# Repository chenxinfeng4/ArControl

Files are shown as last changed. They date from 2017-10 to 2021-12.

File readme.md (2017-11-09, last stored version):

# ArControl Guidence
---
+ Author: Chenxinfeng
+ Email  : chenxinfeng@ibp.hust.edu.cn
+ Copyright (C) 2017, Huazhong University of Science and Technology.  GNU LGPL v2.1.
+ Source-code download: https://github.com/chenxinfeng4/ArControl
+ Binary-release download: https://github.com/chenxinfeng4/ArControl/releases
+ PCB drafts download:  https://github.com/chenxinfeng4/ArControl/releases

## Introduction

---
### What's the ArControl

The goal of ArControl is to establish an Arduino-based (UNO only) behavioral platform, which control devices to deliver stimulation and monitor behavioral response. It's a powerful solution for behavioral researches.

The basic features of this platform include: 

+ Comprehensive – it combines software and hardware, behavioral task design and experimental data collection; 

+ Inexpensive – neither dedicated nor expensive hardware is essential;

+ General purpose – it’s applicable to multiple behavior tasks; 

+ Easy to use – behavior task can be decomposed by the straightforward State Notation concept, and designed via a friendly GUI without need to master script language.

+ Real-time performance – it has high temporal resolution and free from the load of computer.

,



> **Diagram and hardware of the ArControl’s electroniccircuit**. (**a**) Overview of the electronic circuit. Arduino is the core controller detects animal response, sends simulations via digital pin, and logs data to the host computer. ArControl supports 6 input and 8 output digital channels. (**b**) The hardware of ArControl: Arduino Uno R3, the driver circuit for voltage conversion. (**c**) The driver hub provides slots for terminal devices. Sensors can work at 5V, and stimulators can alternatively work at 5/12V.

### ArControl uses State Notation to design tasks

Inspired by Graphic State Notation, we succeeded in grafting State Notation Pattern into ArControl platform (**Figure 2a, b**). The schedule is constructed at hierarchical levels: Session (top), Component (middle), and State (lowest). The State is the basic structure using State Notion design pattern. The Component and the Session are the primary and the secondary collection of States (**Figure 2b**). Generally, the terms of Session, schedule, and behavior task are equal concepts indeed. Utilizing the State Notion Pattern, a schedule is dissembled as a serials of States. Each State specifies a stimulus configuration in subject’s environment and a set of time and/or response requirements that cause state transition (**Figure 2a**). There is one and only one State to be active at any moment. Session will sequentially move from current State to next State, until reaching the terminal. 



>**Figure 2 Diagram of State Notation Pattern utilized by ArControl. **(**a**) The State has a *do-function*
>to deliver stimulus, and *when-functions *to master transitions cross States. (**b**) The Component and Session structures are the primary and secondary collection of States.

### ArControl has tow parts of GUI

The ArControl software suite consists of two individual parts -- the Designer (**Figure 3a**) and the Recorder (**Figure S1a**) -- for the purpose of designing and running a Session respectively. The ArControl Designer is core program, where users apply State Notation concept to achieve the Session construction.

The ArControl Recorder is the other part of ArControl software suite. The basic functions of it contain clicking to start/stop running ready Session, collecting the data flow and displaying as table and chart contents (**Figure S1a**). Besides, there is a straightforward utility tool plugged in —Firmata— intent to debug the input and output devices.

The two parts can run individually. In the source file, they are named as **"arcDersigner.exe"** and **"arcRecorder.exe"**

ArControl GUI logo



> **Figure 3.** Apply ArControl-Designer to design Session. (**a**) The main window of ArControl-Designer.
> It supports two *do-function *and four* when-function* types for each State. (**b, c**) Typical pop-up windows to configure a *do-function *(**b**) and a *when-function *(**c**). (**e**) The layout defines and
> initializes the global variables, which can be share among States.



> **Supplementary Figure 1. The data collection from ArControl. **(**a**) The main window of ArControl-Recorder. (**b**) The serial monitor window of ArControl-Recorder. Numbers after colon represent the beginning and duration time in milliseconds. (**c**) A matched segment extracted from the data file.

## Install ArControl

---
### Download and install Arduino IDE

ArControl relays on Arduino-IDE. You should download the IDE from offical [site](https://www.arduino.cc/en/Main/Software).

- The ArControl was verified on [Arduino IDE 1.6.11](https://www.arduino.cc/en/Main/OldSoftwareReleases#previous) . In theory, the latest versions are also eligible, except 1.6.12.

- You are recommended to download the "Windows Installer" version.

  Arduino logo

### Download and install ArControl

As for general purpose, the [**binary-release**](https://github.com/chenxinfeng4/ArControl/releases) version are recommended. ArControl is only verified on **Microsoft Windows PC**. You can recompile the [**source-code**](https://github.com/chenxinfeng4/ArControl) to make adaptations.

+ If you want to use binary-release directly, just download and unzip it.

+ Onlyif you want to compile source-code, you should download and install [Qt5.7](https://info.qt.io/download-qt-for-application-development). 
+ ArControl will automatically look for any available "Arduino IDE". Make sure that you have installed the "Arduino IDE".

Qt logo

##  Your first task  -- "Light3"
---

### Compose your first task  -- "Light3"

It's nature that different choices lead to different results. It's our first task to follow this schedule (below).  Even a proficient programmer may takes half an hour to implement such schedule, using Arduino C++ langue. However, ArControl makes things easier even for beginners.

shedule

> The sequence of events in **Light3 task**. You will get Yellow Ligth (4sec)  Green Ligth (3 sec) or Red Ligth (2 sec), depending on the your choice of Left, Right or Wait.

The schedule was decomposed with ArControl Designer as figure below. This demo has been embeded in release version, and it can alse be found in `ArControl Designer> File > Open in > Light3`.

Light3

>  The schedule was decomposed with ArControl Designer. Besides, an extra restraint ("max loop = 100 -> Exit Session") were added.

Priority ranks

> Priority ranks (sequences) of `doXXX` and `whenXXX`. Items in `whenPin` are in equal priorities.

Light3 run

> Run a "Light3" task. Data was viewed as log in "Data Stream" pannel, as table in middle pannel, as chart in right pannel, and was collected to data file under "Datafile Folder".

### Insights into the task  -- "Light3"

The `ArControl Designer` saved the previous `Light3` layout as *Light3.aconf*, and automaticaly generated executable *Light3.ino*. 



Light3.ino

The `ArControl Recorder` automatically saved the log to data file. You can use my Matlab function `BF_arc2mat.m` to convert the file from TXT to MAT.





## Other ready demo tasks -- "Go_NoGo" / "2AFPC" task
---
Two common behavior tasks, a Go/No-Go task (Gomez et al., 2007; Dolzani et al., 2013) and a two-choice procedure task (Tai et al., 2012; Stephenson-Jones et al., 2016) which have been widely applied to assess discrimination and memory. Here we implement their logics by ArControl.

### About this two task

The schedules were illustrated as figures below. This demos have been embeded in release version, and can be found in `ArControl Designer> File > Open in > Go_NoGo` and `ArControl Designer> File > Open in > twoAFPC` . 

Go_NoGo schedule

> In the **Go/NoGo task**, mice were body restricted via a head bar and body tube (Guo et al., 2014) and were required to discriminate a go cue (tone) and a no-go cue (light). They would consequently get a reward (water-drop) or a punishment (air-puff) once they respond (lick) to the go cue (tone) or no-go cue (light) during a response window, respectively.

2AFPC task

> In the **2AFPC task**, animals were required to initiate a trial by licking the central port, and sequentially move to a left or a right port to obtain a reward. Only one port was rewarded by 75% at a time. In 25% of trials, neither port was rewarded. If no reward was delivered, animals would be punished with an extra time out. Rewarded port was periodically switched across time.

## Resolution for Common Problems of ArControl Software
---
###  **Recorder Error**: Messages are Messy Coded when uploading a task.
Arduino IDE should be configure as "English" language. Open `Arduino IDE > File > Perferences > Editor language`, choose `English (English)`.

### **Recorder** Error: Crash when uploading a task.
Make sure that you have installed Arduino IDE, the Arduino IDE path is valid. You should renew the path of  Arduino IDE. Open `ArControl Designer > File > Profile > Arduino IDE path`, choose the valid  `arduino_debuger.exe` (for Windows) under the root of  Arduino IDE path.

### Recorder / Designer Error:  Crash immediately when opening

It may caused by wrong configuration of `ArControl`. You should reset the software. Delete `default.bconf` (if exsits), `task\defalut\` (if exsits) and `profile.xml` (if exsits).

### Recorder Error:  A "Time Out" Error when uploading a task.

It's common for a fresh task.  Try to repeat, or try to use `ArControl IDE` to upload the task.

### Recorder Error: Cannot connect to Arduino board

It's common when the Arduino board is currently occupied by other program (etc., `Arduino IDE > Serial Monitor`). Reject the Arduino board from this program, or reconnect via the USB port.

### Recorder Error: "fatal error: xxxxx/ArControl_AllinOne.h: No such file or directory"  when uploading a task

Open  *mytask*.ino, find the line `#include "xxxxxx/ArControl_AllinOne.h"`. The path may be invalid. Renew this path mannually, or resave the *mytask* via `ArControl Designer`.

### How to: Choose language of ArControl
ArControl now merely supports `简体中文` and `English` languages.  Swithing language by -- `ArControl Designer > File > Profile > Language`, `ArControl设计师 > 文件 > 选项 > 语言`.

### How to:  Regard the "whenPin" INx as HIGH or LOW voltage.

Typical sensors reflect resting-status at LOW, and activating-status at HIGH voltage. However, some sensors are opposite coded. Open `Arcontrol Designer > File > Profile > Input signal as`, choose the proper option and it works for all **INx** .

### How to: Start a task immediately or by Hardware-Trigger

A task is commonly triggered by `ArControl Recorder > START` button. However, the task can triggered from other style.  Open `ArControl Designer > File > Profile > "Start" Model`. There are `immediately`, `Trigger by Hardware (pin_11_HIGH)`, `Trigger by: Software (serial communicate)`, `Trigger by: Software or Hardware`.

### How to: Timer-Stop a task

A task is stopped typically from 1. `ArControl Recorder > STOP` button; 2. The task has finished its' schedule (terminates at`C0` or `CxS0`). In addition, you can set a **Timer-Stop** from the `ArControl Recorder > Timer window` .

Timer-Stop

### How to: Use Arduino IDE to run a task

You can use the `ArControl Designer`, as well as `Arduino IDE` to run a task. Open the `Arduino IDE > Serial Monitor`, choose the `250,000 baund` and send the character `b`.

letter b

## Skills and Warns
---

### Warn: Parameters value "`0`"-- special purposing 

Avoid to use `0` as the value of parameter in `ArControl Designer`.

parameters 0

### Skills: Parameters value support Variables 

Global Variables are defined in `Edit > Var Assignment`, dynamicly refreshed in `doVar` or `whenVar`, sharable among States, practicable for parameters value.



### Warn: 20 States are the maximum size of a task

Limited with the 2Kb SRAM of Arduino UNO, 20 States are the maximum size of a Session. 

### Warn: 200 Hz is the maximum frequence of [INx]

ArControl could record 200Hz TTL signal from all 6 input channels simultaneously, and 700Hz when focusing on a single channel, with ±1ms (95% confidence, round effect) accuracy around the truth.

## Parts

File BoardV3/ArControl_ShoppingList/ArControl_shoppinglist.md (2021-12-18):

# ArControl PCB 采购清单
## Arduino Nano (Type-c)
[购买链接](https://item.taobao.com/item.htm?spm=a230r.1.14.12.68d3196cPjnAZf&id=646565255962&ns=1&abbucket=10#detail)

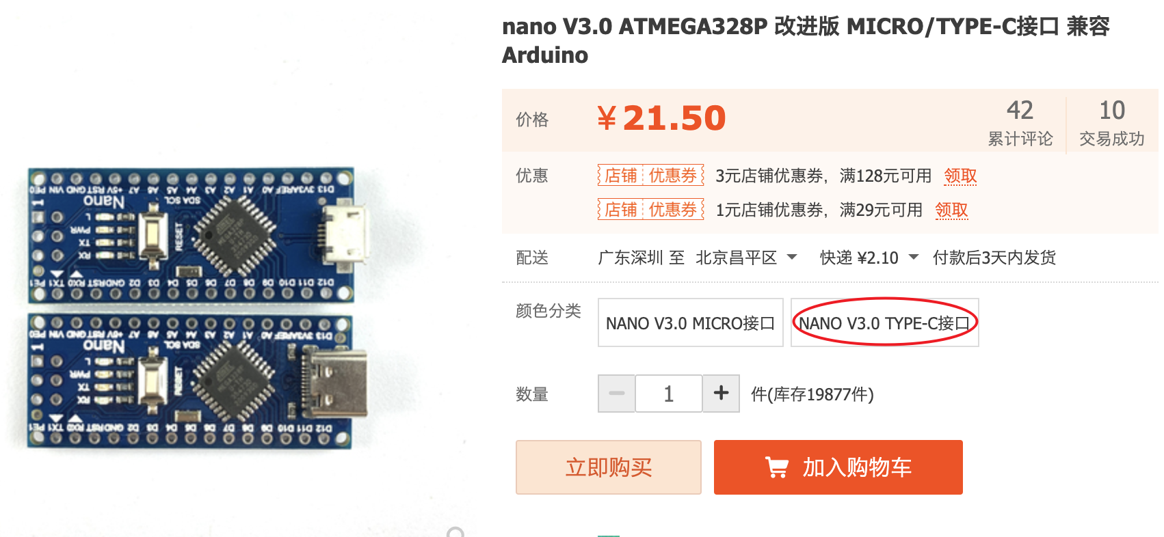
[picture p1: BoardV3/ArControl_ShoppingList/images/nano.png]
demo1


## PCB板打印

[加工链接](http://www.sz-jlc.com/home/factory.html)
+ BoardV3/PCB/Optogentics_Controller.PcbDoc

说明: 收到的是“裸板”，元器件需要自己焊接。

## 外壳3D打印
+ BoardV3/CaseModel/Case1.stl
+ BoardV3/CaseModel/Case2.stl

找淘宝打印

## Type-C数据线
[购买链接](https://detail.tmall.com/item.htm?spm=a220o.1000855.1998025129.2.60eb473cbVLz9X&id=529091830072&scm=1007.12144.95220.23864_0_0&pvid=ef18f5ed-d7ec-41bb-b568-07af17dbfef6&utparam=%7B%22x_hestia_source%22:%2223864%22,%22x_object_type%22:%22item%22,%22x_hestia_subsource%22:%22default%22,%22x_mt%22:0,%22x_src%22:%2223864%22,%22x_pos%22:2,%22wh_pid%22:-1,%22x_pvid%22:%22ef18f5ed-d7ec-41bb-b568-07af17dbfef6%22,%22scm%22:%221007.12144.95220.23864_0_0%22,%22x_object_id%22:529091830072%7D&sku_properties=148242406:21516)

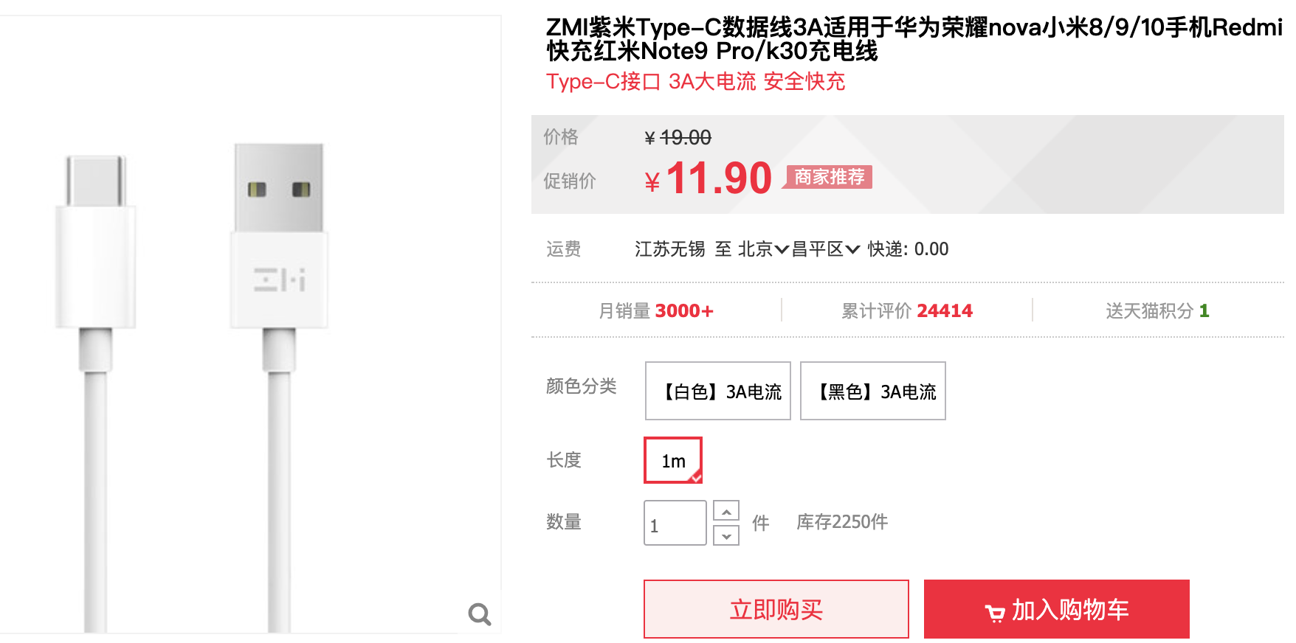
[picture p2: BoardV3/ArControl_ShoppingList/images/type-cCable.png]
demo2


## 三芯 3.5mm音频延长线，转接线
[购买链接](https://item.jd.com/7663022.html)

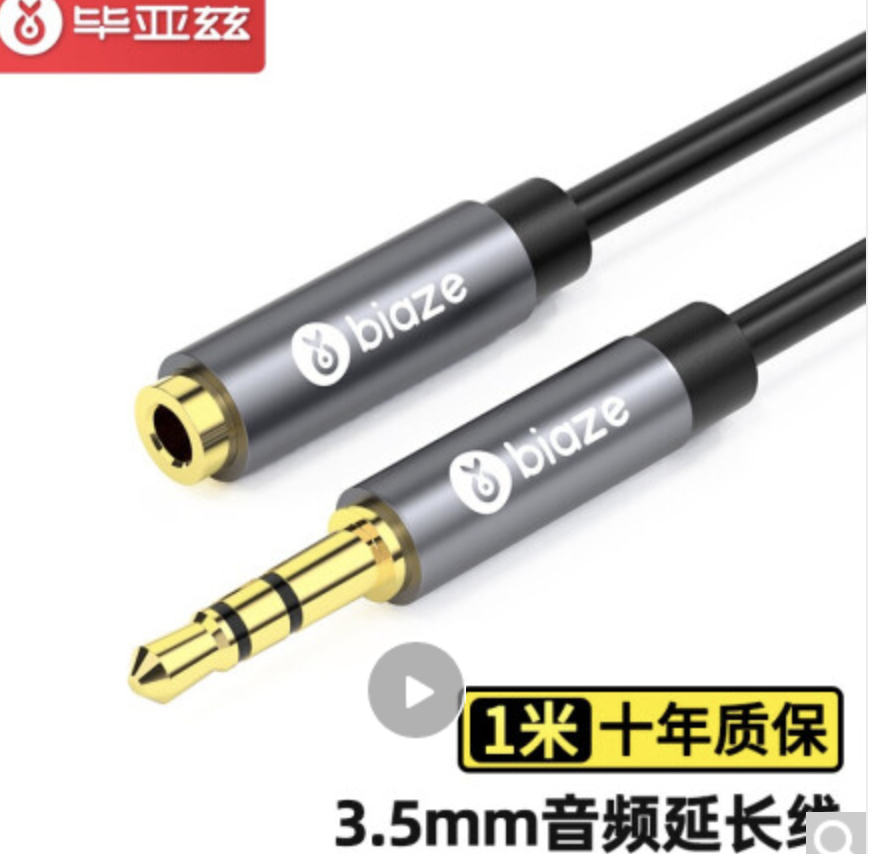
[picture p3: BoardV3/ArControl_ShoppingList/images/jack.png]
demo3


[购买链接](https://item.jd.com/7459184.html)

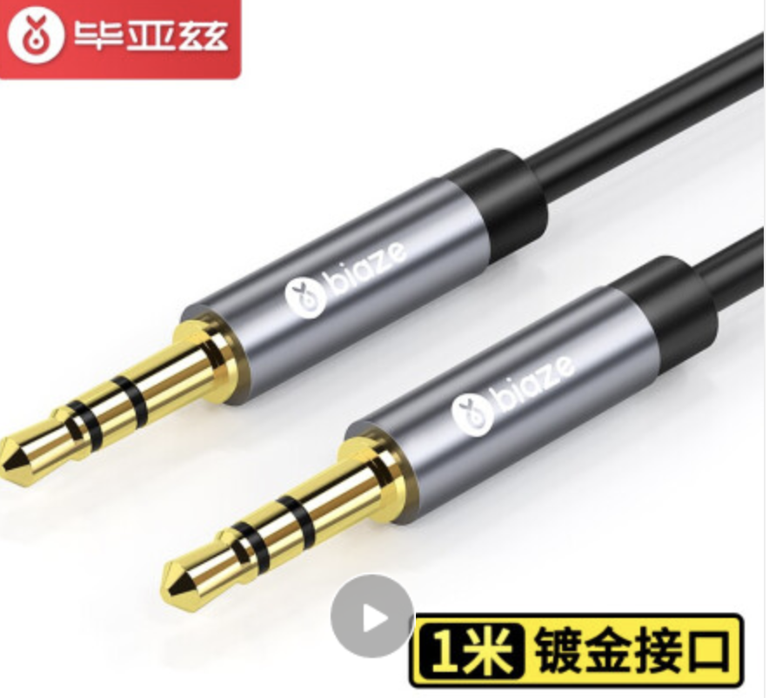
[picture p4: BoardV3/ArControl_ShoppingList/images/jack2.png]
demo4


## 耳机转杜邦线
[购买链接](https://item.taobao.com/item.htm?spm=a1z09.2.0.0.dc0a2e8dHb38ZQ&id=586482384780&_u=impjlclc269)

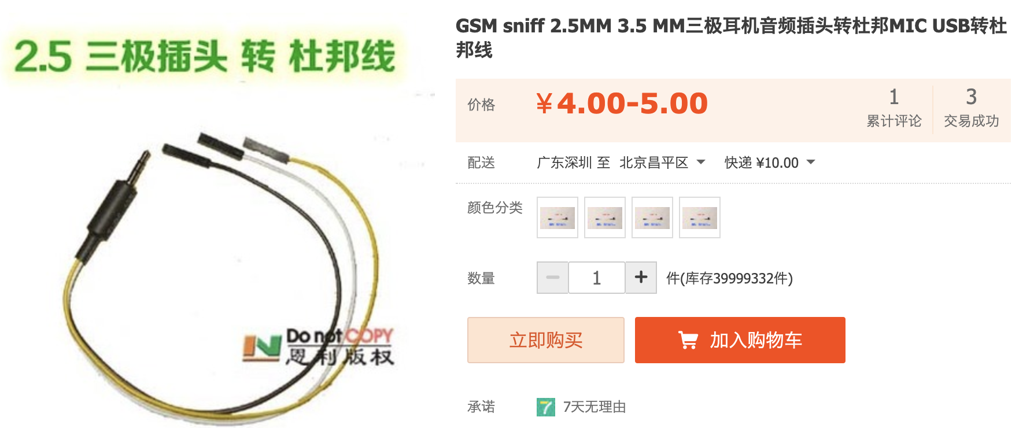
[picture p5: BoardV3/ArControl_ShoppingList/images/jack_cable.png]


--- 
# PCB 板上的元件

## 耳机座
[购买链接](https://item.taobao.com/item.htm?spm=a230r.1.14.36.42a02270QoLXbb&id=566107281055&ns=1&abbucket=10#detail)

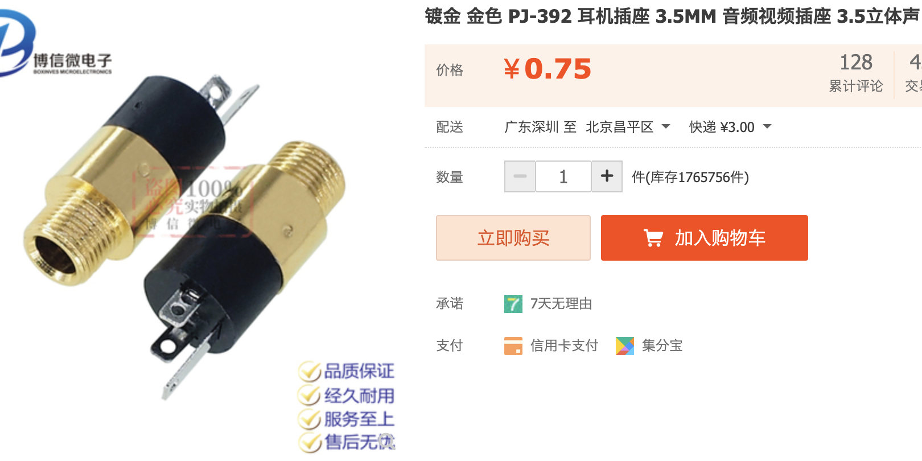
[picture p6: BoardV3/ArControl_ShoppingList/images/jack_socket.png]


## 6位拨码开关
[购买链接](https://item.taobao.com/item.htm?spm=a230r.1.14.27.7aab6226eSfnl2&id=569195865621&ns=1&abbucket=10#detail)

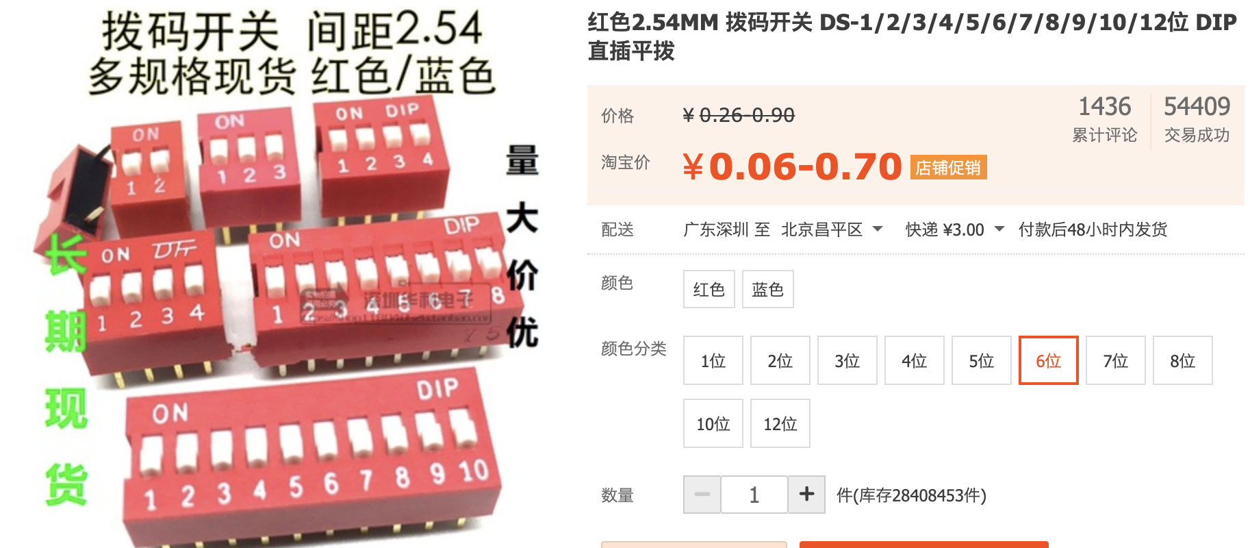
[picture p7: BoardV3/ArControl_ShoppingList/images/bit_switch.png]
demo6


## 单排母
[购买链接](https://item.taobao.com/item.htm?spm=a230r.1.14.16.148e232dNTClwV&id=575511297366&ns=1&abbucket=10#detail)

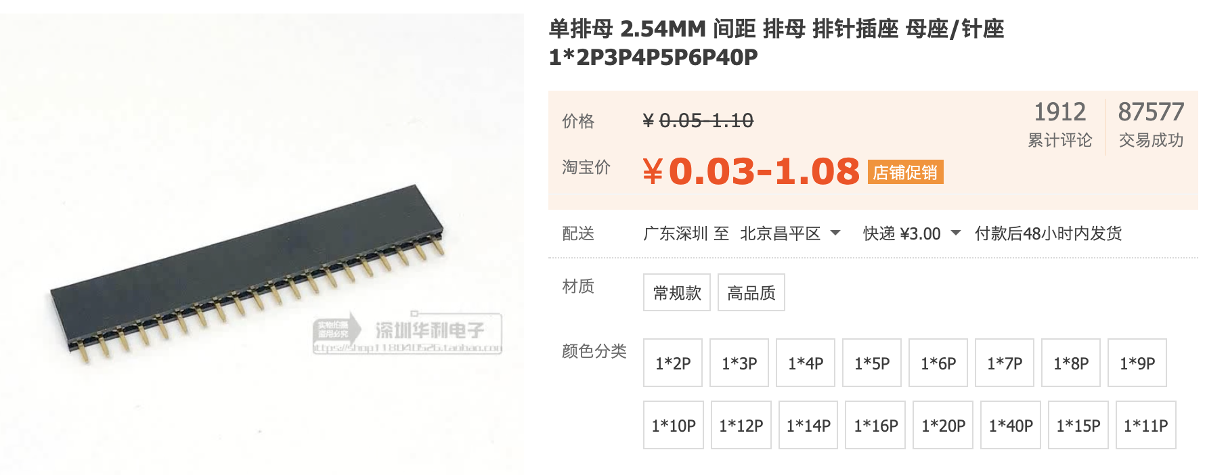
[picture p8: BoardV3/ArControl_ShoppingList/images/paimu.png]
demo7


## 直插LED灯珠
[购买链接](https://item.taobao.com/item.htm?spm=a1z10.3-c-s.w4002-22461697481.9.7e772358qFrZJu&id=575064214996)

demo8

## 贴片电阻
[购买链接](https://detail.tmall.com/item.htm?id=26029684930&spm=a220o.1000855.0.0.yW2MBH)

SMD_Red

推荐用1K

## 贴片LED灯
[购买链接](https://detail.tmall.com/item.htm?id=36030024035&spm=a1z09.2.0.0.GQOEib&_u=7mpjlcl46f3)

SMD_Res

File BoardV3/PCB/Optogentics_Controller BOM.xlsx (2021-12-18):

Description | Designator | Footprint | Quantity | Value
Capacitor (Semiconductor SIM Model) | C1 | 0402 | 1 | 2.2uF
Typical RED, GREEN, YELLOW, AMBER GaAs LED | D1, D2, D3, D4, D5, D6, D7, D8, D9, D10, D11, D12, D13, D14 | 0402-A | 14
Typical RED, GREEN, YELLOW, AMBER GaAs LED | D15, D16 | DIP-LED | 2
Double throw button switch,Non-self-locking | K1, K2, K3, K4, K5, K6, K7, K8 | SW_PB | 8
 | MCU1 | Arduino Nano | 1
Resistor | R1, R2, R3, R4, R5, R6, R7, R8, R9, R10, R11, R12, R13, R14, R15, R16, R17, R18, R19, R20 | 0402 | 20 | 10K
Resistor | R21, R22, R23, R24, R25, R26 | 0402 | 6 | 2K
Resistor | R27, R28, R29, R30, R31, R32, R33, R34, R35, R36, R37, R38, R39, R40, R41, R42 | 0402 | 16 | 820
Resistor | R42 | 0805 | 1 | 10
DIP Switch, 6 Position, SPST | S1 | DIP-12/SW | 1
 | U1, U2 | TSSOP-14 | 2
 | X0 | PWR | 1
3.5mm Audio interface | Xin1, Xin2, Xin3, Xin4, Xin5, Xin6, Xout1, Xout2, Xout3, Xout4, Xou5, Xout6, Xout7, Xout8 | PJ-392 | 14

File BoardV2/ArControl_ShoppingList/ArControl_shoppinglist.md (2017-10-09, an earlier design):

# ArControl PCB 采购清单

材料总金额: **￥384.94**

## Arduino UNO

[购买链接](https://item.jd.com/10223929883.html#crumb-wrap)

ArduinoUNO

说明:  ArControl的核心器件。请购买 UNO(R3), 其它Arduino暂时不适配。请注意购买 USB线。

## PCB板打印

[加工链接](http://www.sz-jlc.com/home/factory.html)

PrintfPCB

说明: 收到的是“裸板”，元器件需要自己焊接。

## 电源适配器 12V 2A

[购买链接](https://detail.tmall.com/item.htm?spm=a220m.1000858.1000725.11.sMIz6P&id=36924057269&areaId=420100&user_id=713464357&cat_id=50069252&is_b=1&rn=89fc3e90cde5a6373ddc1e3a2052a7f5)

AcAdapter

## 线材 

[购买链接](https://item.taobao.com/item.htm?spm=a1z09.2.0.0.GQOEib&id=521015693656&_u=7mpjlcl065c)

wire

说明:  ArControl的PCB板，外接电器 (输入和输出)。

## 排线
[购买链接](https://detail.tmall.com/item.htm?id=542847849062&spm=a1z09.2.0.0.GQOEib&_u=7mpjlcl6010&sku_properties=122216547:20213)

FlatCable

说明: 用于PCB主板连接到次板。

## 牛角座
[购买链接](https://detail.tmall.com/item.htm?id=42188685372&spm=a1z09.2.0.0.GQOEib&_u=7mpjlcla101)

HornsSeat

说明: 与排线配合，连接PCB主板和从板

## 接插件

[购买链接](https://detail.tmall.com/item.htm?id=13300685584&spm=a1z09.2.0.0.GQOEib&_u=7mpjlclb5ed&skuId=3127349611520)

Connector

说明: 位于PCB从板上，用于连接外接电器 (输入和输出)。

## 贴片LED

[购买链接](https://detail.tmall.com/item.htm?id=36030024035&spm=a1z09.2.0.0.GQOEib&_u=7mpjlcl46f3)

SMD_LED

说明: 位于PCB主板上，显示 端口 (输入和输出) 状态。

## 贴片电阻

[购买链接](https://detail.tmall.com/item.htm?id=26029684930&spm=a220o.1000855.0.0.yW2MBH)

SMD_Res

说明: 位于PCB主板上

## 拨动开关
[购买链接](https://detail.tmall.com/item.htm?id=36528897898&spm=a1z09.2.0.0.GQOEib&_u=7mpjlcl46b1)

SlideSwither

说明： PCB主板的OUTPUT手动开关

## 继电器
[购买链接](https://item.taobao.com/item.htm?spm=a1z09.2.0.0.GQOEib&id=535741746982&_u=7mpjlcl0e60)

Relay
说明:  位于PCB主板上，将Arduino的5V电压转化为12V电压。

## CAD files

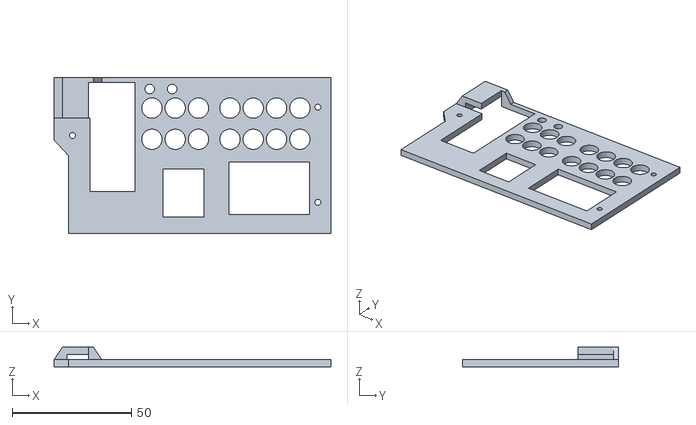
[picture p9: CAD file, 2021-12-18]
BoardV3/CaseModel/Case2.stl
116.0 x 65.5 x 8.25

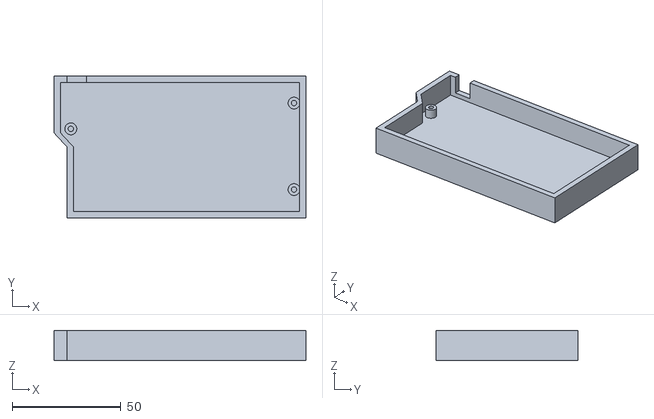
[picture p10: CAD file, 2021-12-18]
BoardV3/CaseModel/Case1.stl
116.0 x 65.5 x 14.0

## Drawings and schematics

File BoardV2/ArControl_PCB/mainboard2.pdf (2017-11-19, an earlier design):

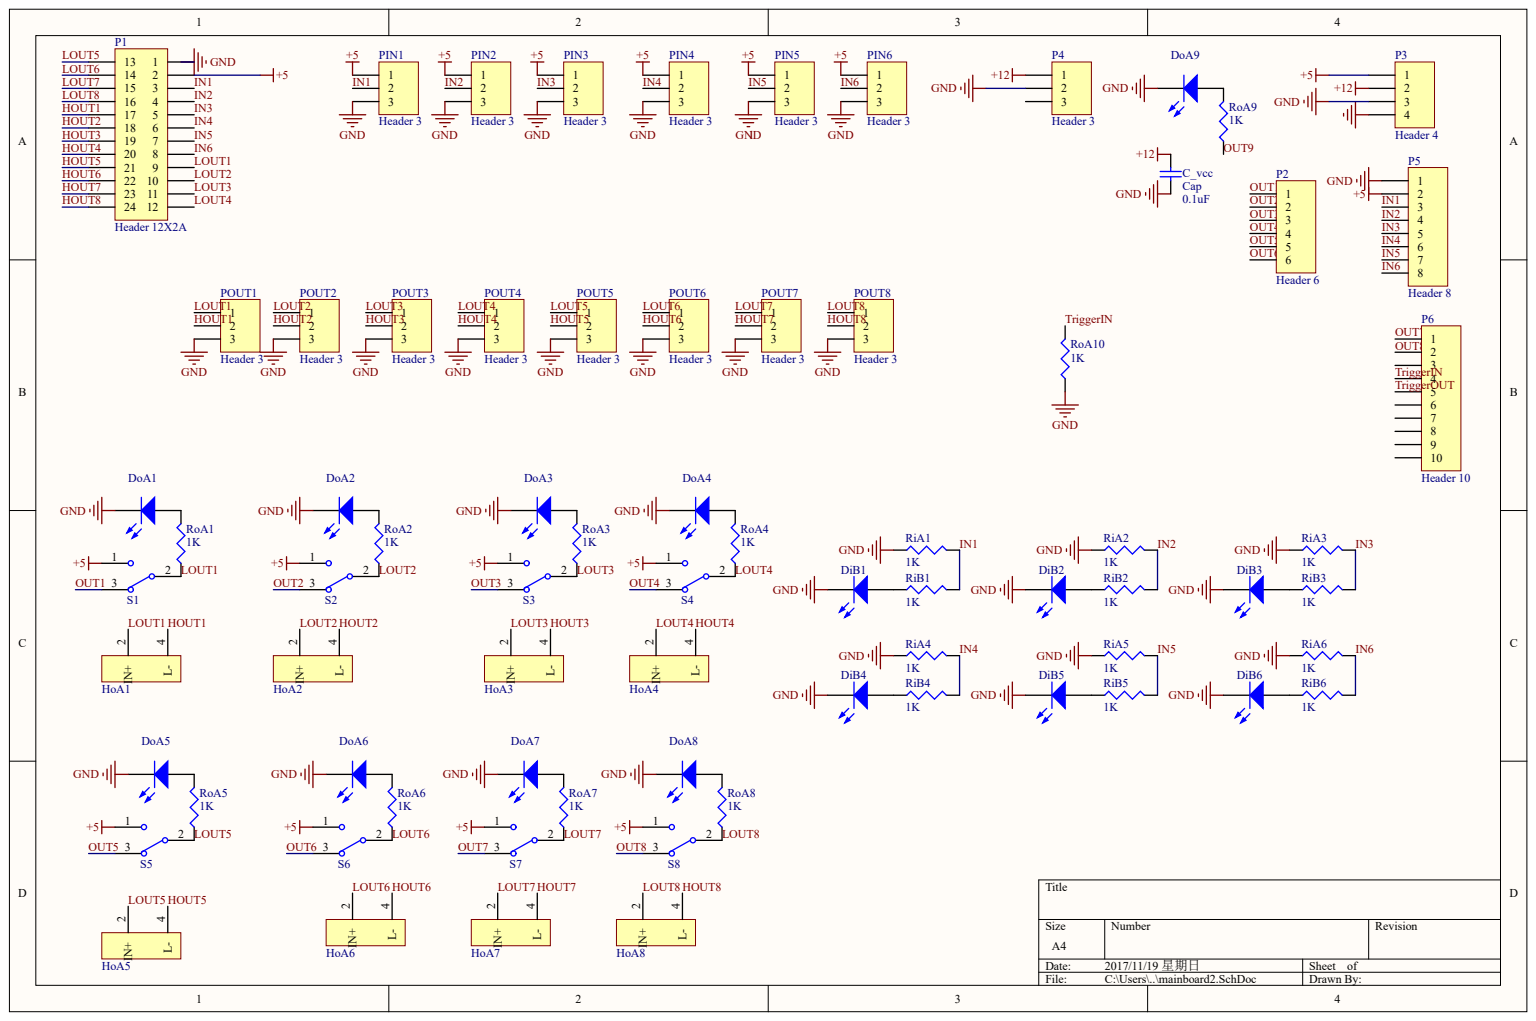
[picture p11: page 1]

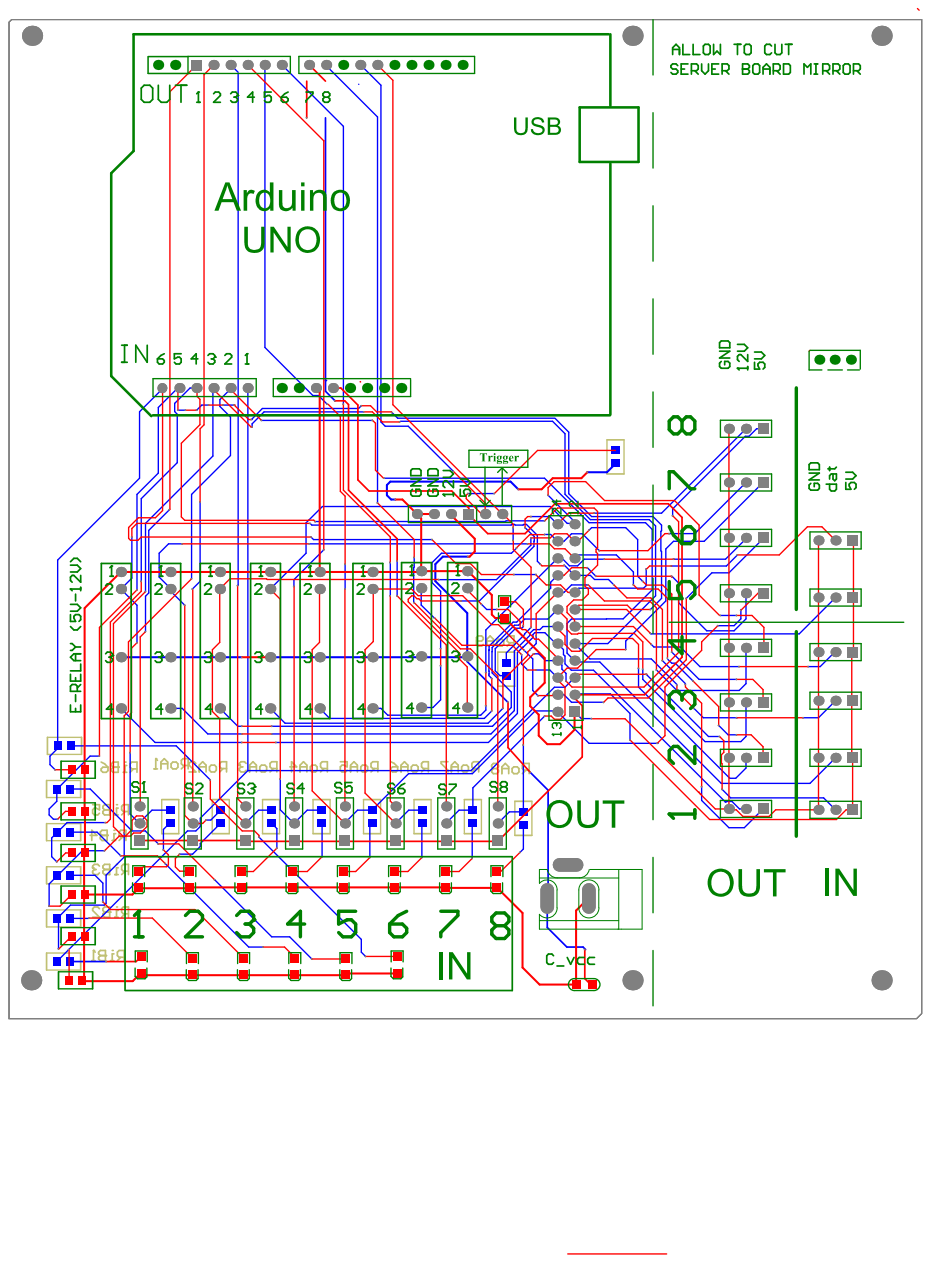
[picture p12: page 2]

Comment | Description | Designator | Footprint | LibRef | Quantity
Cap | Capacitor | C_vcc | 0805C | Cap | 1
LED1 | Typical RED GaAs LED | DiB1, DiB2, DiB3, DiB4, DiB5, DiB6, DoA1, DoA2, DoA3, DoA4, DoA5, DoA6, DoA7, DoA8, DoA9 | LED0805 | LED1 | 15
H3MB-052D | | HoA1, HoA2, HoA3, HoA4, HoA5, HoA6, HoA7, HoA8 | H3MB-052D | H3MB-052D | 8
Header 12X2A | Header, 12-Pin, Dual row | P1 | HDR2X12_CEN | Header 12X2A | 1
Header 6 | Header, 6-Pin | P2 | HDR1X6 | Header 6 | 1
Header 4 | Header, 4-Pin | P3 | HDR1X4 | Header 4 | 1
Header 3 | Header, 3-Pin | P4 | DC005 | Header 3 | 1
Header 8 | Header, 8-Pin | P5 | HDR1X8 | Header 8 | 1
Header 10 | Header, 10-Pin | P6 | HDR1X10 | Header 10 | 1
Header 3 | Header, 3-Pin | PIN1, PIN2, PIN3, PIN4, PIN5, PIN6, POUT1, POUT2, POUT3, POUT4, POUT5, POUT6, POUT7, POUT8 | HDR1X3 | Header 3 | 14
Res3 | Resistor | RiA1, RiA2, RiA3, RiA4, RiA5, RiA6, RiB1, RiB2, RiB3, RiB4, RiB5, RiB6, RoA1, RoA2, RoA3, RoA4, RoA5, RoA6, RoA7, RoA8, RoA9, RoA10 | RESC0805 | Res3 | 22
SW-SPDT | SPDT Subminiature ToggS1, S2, S3, S4, S5, S6, S 7, HDR1X3 | | | SW -SPDT | 8

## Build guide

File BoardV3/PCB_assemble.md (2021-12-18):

# ArControl PCB Assemble

- Author: Xinfeng Chen (陈昕枫)

- Email  : chenxinfeng@pku.edu.cn

- Cite This:

  > Xinfeng Chen, Haohong Li. 2017. ArControl: An Arduino-based comprehensive behavioral platform with real-time performance. (In Press)

## The Finished Product of PCB

---

You're recommended to construct  the `ArControl_PCB/mainboard_V3` as below. You can use it to monitor **INs** and control **OUTs**  through the identical **Connecters**. 

The **shopping list** , in `ArControl_ShoppingList`, is directly available in *China*.  

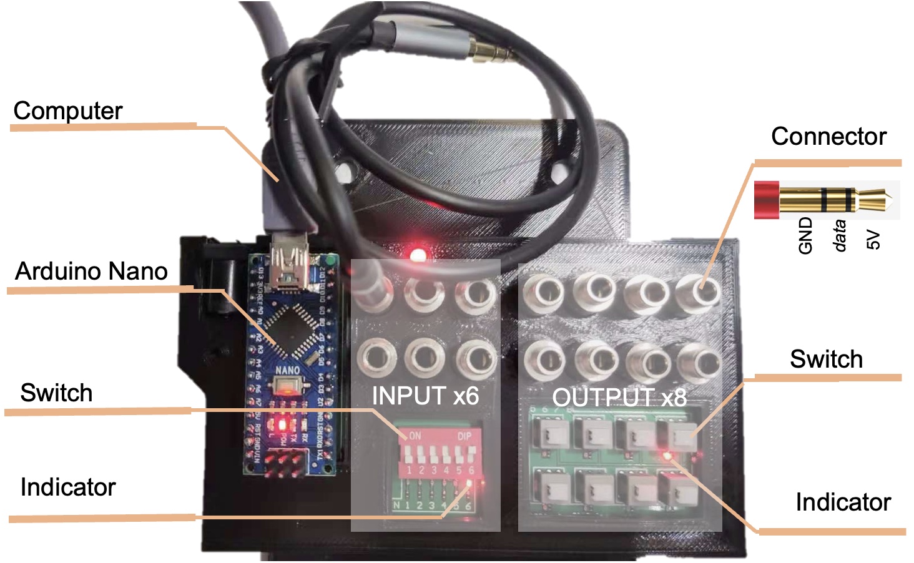
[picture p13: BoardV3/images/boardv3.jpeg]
demo1


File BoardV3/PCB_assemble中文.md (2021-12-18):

# ArControl PCB Assemble

- 作者: 陈昕枫

- 邮件  : chenxinfeng@pku.edu.cn

- 引用:

  > Xinfeng Chen, Haohong Li. 2017. ArControl: An Arduino-based comprehensive behavioral platform with real-time performance. (In Press)

## PCB成品

---

建议您使用`ArControl_PCB/mainboard_V3`目录下的PCB，最后组装的效果如下图。您可在在 **IN** 和 **OUT** 标注的连接槽连接相应的设备。

关于购买**元器件清单**，您可以在`ArControl_ShoppingList`目录下找到。

或者可以发邮件给我 chenxinfeng@pku.edu.cn ，说明用意，索取1个。
demo1

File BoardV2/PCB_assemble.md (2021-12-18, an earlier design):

# ArControl PCB Assemble

- Author: Xinfeng Chen (陈昕枫)

- Email  : chenxinfeng@hust.edu.cn

- Cite This:

  > Xinfeng Chen, Haohong Li. 2017. ArControl: An Arduino-based comprehensive behavioral platform with real-time performance. (In Press)

## 1. The Finished Product of PCB

---

You're recommended to construct  the `ArControl_PCB/mainboard_V2` as below. You can use it to monitor **INs** and control **OUTs**  through the identical **Connecters**. 

The **shopping list** , in `ArControl_ShoppingList`, is directly available in *China*.  Though it's cheap and easy, this type of **Electric Relay** ("Ingenex 1703D H3MB-052D") may be inaccessible outside *China*. Still, it could be replaced, such as "Kyoto Electric KF0602D DC-to-DC Solid State Relay" in Amazon.

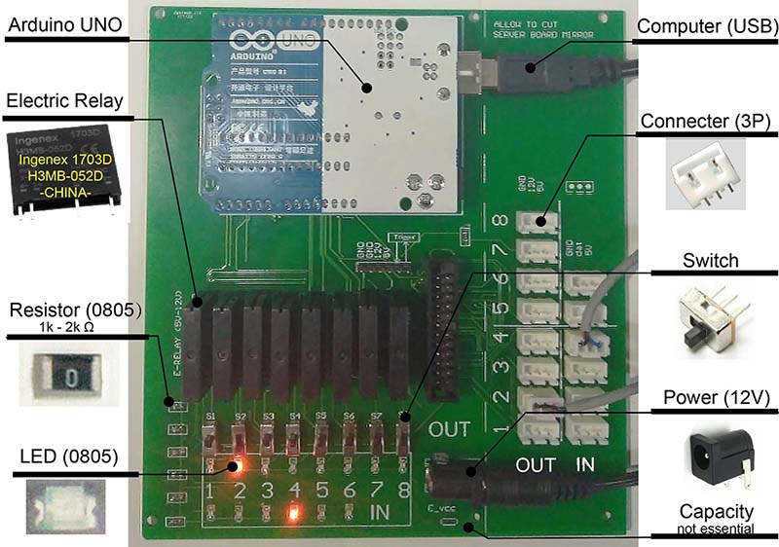
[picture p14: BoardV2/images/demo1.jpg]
demo1


> Construction of the ArControl PCB (mainboard_V2).

## 2. Discriminate LEDs and Resistors

---

Be careful that the prints of LEDs and Resisitors are quite similar.

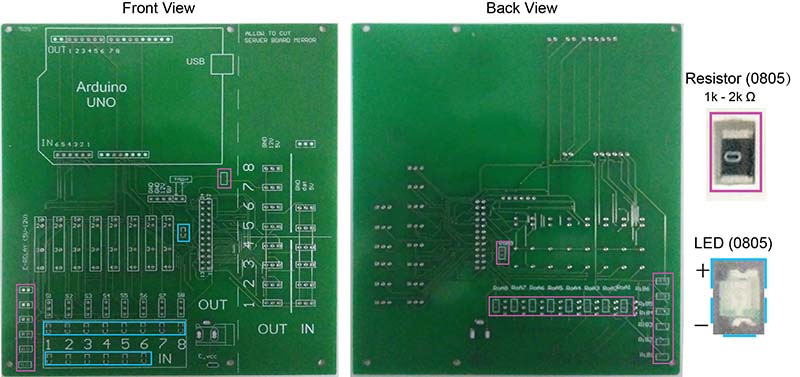
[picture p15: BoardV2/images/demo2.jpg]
demo2


> The front view and the back view of PCB. The colored rect-lines are specified for LED or Resistor.

## 3. Device Connector

---

The input and output devices are marked as *IN 1-6* and *OUT 1-8*, where they are identically managed managed through ArControl Software and powered by the **Device Connectors**.

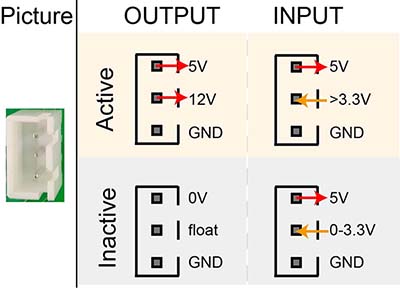
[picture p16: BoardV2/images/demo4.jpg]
demo4


> Structure of Device Connector.

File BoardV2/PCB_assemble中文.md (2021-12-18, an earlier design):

# ArControl PCB 组装

- 作者: 陈昕枫

- 邮箱: chenxinfeng@pku.edu.cn

## 1. PCB成品

---

建议您使用`ArControl_PCB/mainboard_V2`目录下的PCB，最后组装的效果如下图。您可在在 **IN** 和 **OUT** 标注的连接槽连接相应的设备。

关于购买**元器件清单**，您可以在`ArControl_ShoppingList`目录下找到。里面的元器件都是在中国国内能购买到的。国外的同仁如果无法购买到**继电器**("Ingenex 1703D H3MB-052D")，则可使用 Amazon 上的"Kyoto Electric KF0602D DC-to-DC Solid State Relay" **继电器**进行等效替代。

demo1

> ArControl PCB (mainboard_V2) 的完成图。

## 2. 辨别贴片 LED 和电阻

---

这两者的封装很相近，焊接时请一定要分清。

demo2

> PCB裸板的前与后视图。颜色框分别标注了 LED 和电阻的位置。

## 3. 从板

---

您可以在 `ArControl_PCB/serverboard` 中找到**从板**，它利于延长电器设备与主要板的连接距离。但是**从板**并不是必须的，它的功能已被主要板集成了。

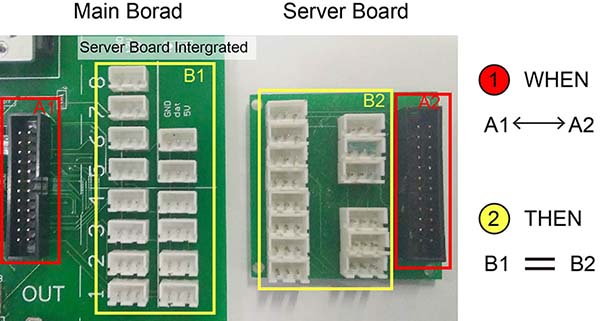
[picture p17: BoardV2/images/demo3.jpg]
demo3


> 从板的完成图。

## 4. 设备连接槽

---

ArControl使用 IN1-6 和 OUT1-8 来标注输入设备和输出设备。它们统一由软件来控制，由硬件来驱动。

demo4

> 设备连接槽的工作示意图。

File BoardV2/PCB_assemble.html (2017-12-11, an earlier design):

# ArControl PCB Assemble

- Author: Xinfeng Chen (陈昕枫)
- Email : chenxinfeng@hust.edu.cn
- Cite This:
  Xinfeng Chen, Haohong Li. 2017. ArControl: An Arduino-based comprehensive behavioral platform with real-time performance. (In Press)

## 1. The Finished Product of PCB

You're recommended to construct the ArControl_PCB/mainboard_V2 as below. You can use it to monitor INs and control OUTs through the identical Connecters.

The shopping list , in ArControl_ShoppingList, is directly available in China. Though it's cheap and easy, this type of Electric Relay ("Ingenex 1703D H3MB-052D") may be inaccessible outside China. Still, it could be replaced, such as "Kyoto Electric KF0602D DC-to-DC Solid State Relay" in Amazon.

demo1

Construction of the ArControl PCB (mainboard_V2).

## 2. Discriminate LEDs and Resistors

Be careful that the prints of LEDs and Resisitors are quite similar.

demo2

The front view and the back view of PCB. The colored rect-lines are specified for LED or Resistor.

## 3. Server Board

The Server Board, in ArControl_PCB/serverboard, is a simple hub that makes long connecting easier. However, since its function has been intergrated into the Main Board, the Server Board is not essential.

demo3

View of Server Board.

## 4. Device Connector

The input and output devices are marked as IN 1-6 and OUT 1-8, where they are identically managed managed through ArControl Software and powered by the Device Connectors.

demo4

Structure of Device Connector.

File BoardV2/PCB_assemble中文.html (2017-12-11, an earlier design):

# ArControl PCB 组装

- 作者: 陈昕枫
- 邮箱: chenxinfeng@hust.edu.cn

## 1. PCB成品

建议您使用ArControl_PCB/mainboard_V2目录下的PCB，最后组装的效果如下图。您可在在 IN 和 OUT 标注的连接槽连接相应的设备。

关于购买元器件清单，您可以在ArControl_ShoppingList目录下找到。里面的元器件都是在中国国内能购买到的。国外的同仁如果无法购买到继电器("Ingenex 1703D H3MB-052D")，则可使用 Amazon 上的"Kyoto Electric KF0602D DC-to-DC Solid State Relay" 继电器进行等效替代。

demo1

ArControl PCB (mainboard_V2) 的完成图。

## 2. 辨别贴片 LED 和电阻

这两者的封装很相近，焊接时请一定要分清。

demo2

PCB裸板的前与后视图。颜色框分别标注了 LED 和电阻的位置。

## 3. 从板

您可以在 ArControl_PCB/serverboard 中找到从板，它利于延长电器设备与主要板的连接距离。但是从板并不是必须的，它的功能已被主要板集成了。

demo3

从板的完成图。

## 4. 设备连接槽

ArControl使用 IN1-6 和 OUT1-8 来标注输入设备和输出设备。它们统一由软件来控制，由硬件来驱动。

demo4

设备连接槽的工作示意图。

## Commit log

2017-10-09 initial for window relase version
    [mainboard.PrjPCB, mainboard.SchDoc, serverboard.PcbDoc, serverboard.PrjPCB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]
2017-11-09 fix PCB bug; optimize PCB
    [mainboard.PrjPCB, mainboard.SchDoc, mainboard2.PrjPCB, mainboard2.SchDoc]
2017-11-19 optimize the PCB
    [mainboard2.PrjPCB, mainboard2.SchDoc]
2017-12-06 Add guidence for PCB assemble.
2017-12-06 Arrange PCB files.
    [mainboard.PrjPCB, mainboard.SchDoc, mainboard2.PrjPCB, mainboard2.SchDoc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]
2021-12-18 add BoardV3
    [Case1.stl, Case2.stl, Optogentics_Controller BOM.xlsx, Optogentics_Controller.PcbDoc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]
2021-12-19 update boardv3 figure
